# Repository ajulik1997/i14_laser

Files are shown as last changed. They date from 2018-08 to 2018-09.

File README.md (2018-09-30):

# I14 Remote Laser Controller

Software developed for the remote control and monitoring of a laser at the [Diamond Light Source I14 instrument](https://www.diamond.ac.uk/Instruments/Imaging-and-Microscopy/I14.html).

The following documentation is designed as a guide to simplify the processes of preparing the hardware and installing this software, as well as extending its functionality and applying it to other components or instruments.

## Table of Contents

- [Introduction](#introduction)
  - [Key Features](#key-features)
- [The Hardware](#the-hardware)
  - [Raspberry Pi](#raspberry-pi)
    - [Operating System](#operating-system)
    - [Drivers and Packages](#drivers-and-packages)
    - [Python](#python)
    - [Pin Assignment](#pin-assignment)
  - [Laser](#laser)
  - [Arduino](#arduino)
    - [Pin Assignment](#pin-assignment)
    - [LED Signalling](#led-signalling)
    - [Wiring Diagram](#wiring-diagram)
  - [Digital to Analog Converter](#digital-to-analog-converter)
    - [Safety](#safety)
    - [Laser modulation](#laser-modulation)
  - [Camera](#camera)
- [The Software](#the-software)
  - [Server](#server)
    - [Client](#client)
  - [Parser](#parser)
    - [Table of Recognised Commands](#table-of-recognized-commands)
  - [Error Handler](#error-handler)
    - [Table of Errors and Warnings](#table-of-errors-and-warnings)
  - [Laser Serial Communication Script](#laser-serial-communication-script)
  - [Arduino Controller Script (Python)](#arduino-controller-script-python)
    - [Arduino Controller Script (C for AVR)](#arduino-controller-script-c-for-avr)
- [Licensing](#licensing)
- [Author](#author)
- [Acknowledgements](#acknowledgements)

## Introduction

At the core of this "system" lies a [Raspberry Pi](https://www.raspberrypi.org/), used as a server running a python script which allows it to process text-based commands that it receives over network. A [Coherent Laser](https://www.coherent.com/) is connected to the Raspberry Pi via a USB-to-Serial interface, enabling the Pi to send commands to the laser and monitor its status. An [Arduino board](https://www.arduino.cc/) is also connected to the Raspberry Pi via a USB-to-Serial as well as a GPIO interface, and is mainly responsible for real-time generation of waveforms that are used to modulate the laser via a Digital-to-Analog converter (DAC). Additionally, a camera can also be connected to the Arduino, which can synchronise the camera's shutter with the modulation of the laser.

A diagram that illustrates this setup can be seen below. It was created using [draw.io](https://www.draw.io/), and the source can be downloaded [here](./resources/flowcharts/project_map.xml).

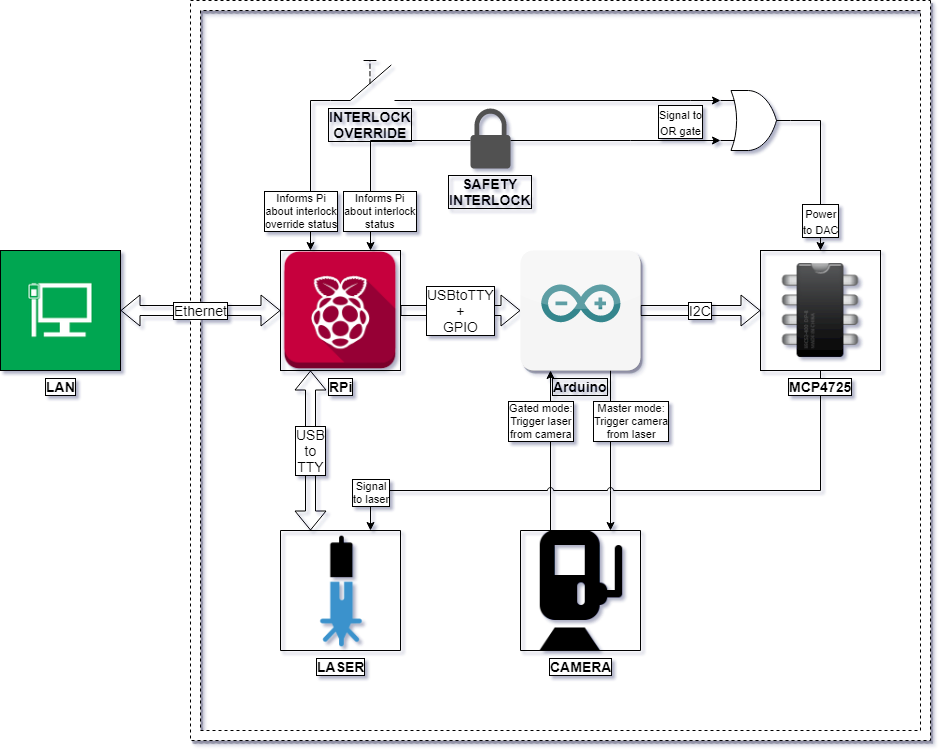
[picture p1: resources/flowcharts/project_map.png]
Project Map


### Key Features

The most noteworthy and desirable features of this project can be summarised as follows:

  - Remote control of laser over LAN
  - Remote monitoring of laser and safety interlock status over LAN
  - High-precision control of laser output intensity
  - Modulation of laser beam with pre-set waveforms of customisable period length and inter-cycle delay:
    - Sine wave, triangle wave, sawtooth wave: cycle period between 1 millisecond and 1 second
    - Square wave, pulse wave: cycle period between 1 millisecond and 1 hour
  - Synchronisation of laser with connected camera:
    - "gated mode": laser is turned on only when camera is exposing
    - "master mode": camera exposure triggered when laser intensity reaches a customisable threshold
  - Robust and extensible error handling
  - Modular, well-documented code for easy customisation

## The Hardware

The following section documents the steps required to correctly set up the hardware. It describes the setup of the operating system on the Raspberry Pi, as well as the required wiring between the Raspberry Pi, Arduino, DAC, laser and camera.

### Raspberry Pi

The Raspberry Pi used in this project is the [Raspberry Pi 3 B+](https://www.raspberrypi.org/products/raspberry-pi-3-model-b-plus/) (upgraded from the Raspberry Pi B Rev 2.0 on which development took place), chosen due to the following features:
  - 1.4GHz processor (upgraded from 700MHz)
  - 1GB SDRAM (upgraded from 512MB)
  - 40 GPIO pins (upgraded from 26)
  - Gigabit Ethernet
  - MicroSD port
  - PoE support

According to our specification, the Raspberry Pi needs to be set up so that it can do the following:
  - run a headless Linux OS
  - securely connect to a LAN
  - communicate with other devices on the LAN via SSH
  - communicate with laser via Serial-over-USB
  - communicate with Arduino via Serial-over-USB and GPIO
  - start Python server at boot and ensure it restarts on exit

#### Operating System

The operating system chosen for this project was [Raspbian Stretch Lite](https://www.raspberrypi.org/downloads/raspbian/), an OS based on Debian Stretch with no desktop interface, chosen for its minimal footprint and high compatibility with Raspberry Pi. The required image was downloaded from the [official mirror](https://downloads.raspberrypi.org/raspbian_lite_latest), and written to a 16GB microSD card according to the [installation instructions](https://www.raspberrypi.org/documentation/installation/installing-images/README.md).

As the Pi is being used a server, it needs to be set up to run headless. This process is described in detail [here](https://www.raspberrypi.org/documentation/configuration/wireless/headless.md), but the most important step (activating SSH), can be accomplished by mounting the boot partition of the SD card on any device and creating an empty file with the filename `ssh`. The contents of this file does not matter, as it will be deleted on boot, and SSH should be activated. Alternatively, it is possible to do the initial setup with an attached monitor and keyboard. Note that, on some networks, the MAC address of the Raspberry Pi will first need to be registered before any network communication can take place. In this scenario, using a monitor and keyboard initially is the easiest option.

Once it is possible to interface with the Raspberry Pi, either over SSH or physically, the Raspberry Pi configuration tool will need to be launched using:

```shell
sudo raspi-config
```

You will be presented with a terminal user interface (TUI) similar to the one below:

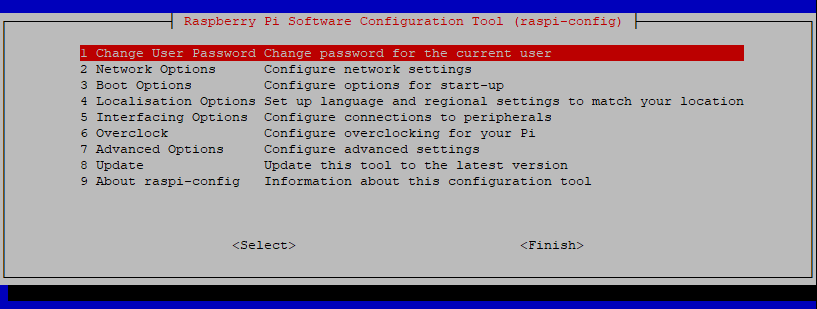
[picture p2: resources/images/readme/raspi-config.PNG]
raspi-config


The settings that will need be changed are:
  - **Change User Password**: change the user password so that it is not possible to start an SSH session with the Raspberry Pi using the default password
  - **Network Options**:
    - **Hostname**: change the name that the Raspberry Pi identifies itself as on the network (default is `raspberrypi`)
  - **Interfacing Options** (optional):
    - **Camera**: disable the CSI camera interface as we are not using it
    - **SSH**: enable the SSH interface if you have not done so already
    - **VNC**: disable the VNC as we are not running a desktop environment
    - **SPI**: disable the SPI interface and automatic loading of the SPI kernel module as we are not using it
    - **I2C**: disable the I2C interface and automatic loading of the I2C kernel module as we are not using it
    - **1-Wire** : disable the 1-Wire interface as we are not using it

If the device will only communicate over Ethernet, then we can disable WiFi and Bluetooth by adding the following lines to `/boot/config.txt`:

```shell
dtoverlay=pi3-disable-wifi
dtoverlay=pi3-disable-bt
```

Once Bluetooth has been disabled, `systemd` will encounter an error when loading the `hciuart` service. Although this error is harmless, in order to avoid the error message at boot, you can do:

```shell
sudo systemctl disable hciuart
```

Optionally, it is a good idea to disable all other services that we will not need. A full list of active `systemd` services is obtained by running `sudo systemctl list-unit-files | grep enabled`. Please inspect this list **carefully** before disabling all but the services you require. I have found that the following services are critical for normal operation of a minimal Raspberry Pi system:

- `autovt`: configures and manages virtual terminals
- `cron`: time-based job scheduler
- `dbus`: inter-process communication and message bus system
- `dhcpcd`: provides a DHCP service
- `fake-hwclock`: emulates a hardware clock on systems that don't have or support one
- `getty`: short for "get TTY", it manages physical or virtual terminals
- `networking`: manages all networking interfaces
- `rsyslog`: manages system logging
- `ssh`: SSH service
- `systemd`: system and service manager for Linux

To disable all enabled services except those listed above, execute:

```shell
sudo systemctl list-unit-files \
  | grep enabled \
  | cut -f 1 -d ' ' \
  | grep -v -E 'autovt|cron|dbus|dhcpcd|fake-hwclock|getty|networking|rsyslog|ssh|systemd' \
  | while read -r line; do sudo systemctl disable $line; done
```

To install an NTP client on the Raspberry Pi:

```shell
sudo apt-get update && sudo apt-get install ntp
```

If the Raspberry Pi is connected to a network without access to an NTP server, or you want to set the time before connecting to a network, you can do so with the following command:

```shell
sudo date -s "DD MMM YYYY HH:MM:SS"
```

##### Firewall setup

Firewall rules for the Raspberry Pi also need to be set up. Firstly, the default behaviour should be that the Pi will drop all incoming and forwarded packets, but allow all outgoing packets:

```shell
iptables -P INPUT DROP
iptables -P FORWARD DROP
iptables -P OUTPUT ACCEPT
```

Secondly, we should enable all communication on the `loopback` interface:

```shell
iptables -A INPUT -i lo -j ACCEPT
iptables -A OUTPUT -o lo -j ACCEPT
```

Additionally, we should allow all established sessions to communicate freely on the network:

```shell
iptables -A INPUT -m conntrack --ctstate ESTABLISHED,RELATED -j ACCEPT
```

Finally, we add exceptions to the default behaviour by allowing the following incoming packets:

```shell
iptables -A INPUT -p tcp --dport 22 -j ACCEPT       # SSH
iptables -A INPUT -p tcp --dport 14000 -j ACCEPT    # Python server
iptables -A INPUT -p udp --dport 123 -j ACCEPT      # NTP
iptables -A INPUT -p udp --dport 67:68 -j ACCEPT    # DHCP
```

##### Default user setup

It may be useful to also change the name and home directory of the default user from the default `pi`. To do this, first log in as the user `pi` and enable the `root` account by changing its password using `sudo passwd root` and entering a new password. Then, reboot the Raspberry Pi and log in as `root`, then execute:

```shell
usermod -l pi new_username
usermod -m -d pi new_username
```

Note that, these two commands cannot be carried out the same time according to the [documentation](https://linux.die.net/man/8/usermod), as changing the login name and the user's home directory have to be carried separately.

After that is done, reboot the system and log in to your new user account. From that account, you can again disable the `root` account by doing the following:

```shell
sudo su -c "usermod -L -e 1 root"
```

#### Drivers and Packages

This section highlights the packages and drivers that need to be installed or set up, either as dependencies by the server, or optional add-ons for easier development and set-up.

##### Flashing '.hex' files to Arduino

As of Arduino 1.6, it is possible to develop Arduino applications directly on the Raspberry Pi, although this is not recommended, as the newly released Arduino CLI has too many dependencies (up to 1GB, including a desktop environment, which is not necessary on a headless Raspberry Pi) for a system with limited storage and memory. Instead, it is recommended that all Arduino development is carried out elsewhere, and the compiled `.hex` can be sent to the Raspberry Pi via `scp`, then flashed onto the Arduino from the Raspberry Pi using `avrdude`.

`avrdude` is a software for programming Atmel AVR controllers, such as the ATmega328 that is at the core of the Arduino Duo. At the time of writing, `avrdude` was available for download using `apt-get`:

```shell
sudo apt-get install avrdude
```

Alternatively, you can download the latest source code from [here](http://download.savannah.gnu.org/releases/avrdude/), and compile from source.

Flashing a `.hex` file can then be accomplished by running the following command, explained below:

```shell
sudo avrdude -p atmega328p -P /dev/ttyACM0 -c arduino -U flash:w:arduino.hex:i
```

- `sudo` to give `avrdude` permission to access the USB device
- `-p atmega328p` to select the part number of the microcontroller (atmega328p for my Arduino Uno)
- `-P /dev/ttyACM0` to specify the communication port (change this if your Arduino is assigned a different port)
- `-c arduino` to specify the programmer type (`arduino` is the safest option, but a different setting may be needed depending on your chip)
- `-U flash:w:arduino.hex:i` is the command that does the actual programming
  - `flash` is the memory type we are flashing
  - `w` specifies write mode (which usually also carries out a verify pass after flashing)
  - `arduino.hex` is the filename of the `.hex` file we are flashing (change this to your filename)
  - `i` specifies that this file has the “Intel Hex” format

Many other options are also available, that may or not may be useful or necessary when doing your own development. A nice tutorial that highlights all the important options can be found [here](http://www.ladyada.net/learn/avr/avrdude.html).

##### Setting up USB laser as a Serial device

When the laser is first plugged in to the Arduino, it is not recognised as a device capable of serial input/output. Although the laser uses a standard FTDI chip, its VID/PID is not one recognised by Linux as a `ftdi_sio` device. Luckily, most modern Linux distributions (including Raspbian) have FTDI drivers built into their Kernel.

We start by creating a shell script `laserUSBtoSerial.sh` (alternatively, you can download it from [here](./laserUSBtoSerial.sh)):

```shell
#!/bin/bash
modprobe ftdi_sio
echo 0d4d 003d > /sys/bus/usb-serial/drivers/ftdi_sio/new_id
udevadm control --reload && udevadm trigger
```

`modprobe` adds an `ftdi_sio` module into the Linux kernel. Using `echo`, we then insert the Vendor ID (`0d4d` - registered by Coherent) and the Product ID (`003d` - specific to this laser model) into a file newly created by `modprobe`. This allows the kernel to associate a device that identifies itself using that VID/PID combination (our laser) with the relevant FTDI driver. Finally, for a change to be detected by the kernel, the USB device needs to unplugged (if it is plugged in), and re-plugged. If physical access to the device is not available as expected, `udevadm` is used to reload the udev rules and trigger a USB plug-in event.

This script needs to be executed with superuser privileges after every reboot:

```shell
sudo su -c "./laserUSBtoSerial.sh"
```

In order to avoid having to manually run the script, it is recommended to install it a `systemd` service that will run this script once at boot.

We will create a `.service` file in the path `/lib/systemd/system/` called `laserUSBtoSerial.service` as follows (or download it from [here](./laserUSBtoSerial.service)):

```shell
[Unit]
Description=Enable Coherent Laser USB-to-Serial

[Service]
Type=forking
ExecStart=/home/pi/laserUSBtoSerial.sh

[Install]
WantedBy=multi-user.target
```

For the sake of brevity, the options specified in this `systemd.service` file will not be explained here. Instead, a page that gives in-depth explanations and usage examples of all the available options can be viewed [here](https://www.freedesktop.org/software/systemd/man/systemd.service.html).

Once the file is created, its permission will need to be changed to allow execution:

```shell
sudo chmod 744 laserUSBtoSerial.sh
```

Finally, the `.service` will need to be enabled:

```shell
sudo systemctl enable laserUSBtoSerial.service
```

At this point, the service should be set up to execute our script at boot. To test whether the service is configured properly, you can execute `sudo systemctl start laserUSBtoSerial` , or simply reboot the device. Then, check the status of the service using `sudo systemctl status laserUSBtoSerial` (the presence of any errors will be highlighted in red, and point to an incorrect setup of the service).

#### Python

The server for the Raspberry Pi was written in `Python3` and tested on `3.5.3`, which was the version that came preinstalled with operating system. The list of non-trivial libraries that the server and parser depend on are:

- `RPi.GPIO`: for control of GPIO pins
- `serial`: for serial communication with connected devices
- `socket`: needed for accessing the BSD socket interface
- `threading`: needed for a threaded server

Out of these, `RPi.GPIO` and `serial` are not included in Python's Standard Library (`RPi.GPIO`, however, comes preinstalled for `Python2` with Raspberry Pi). These libraries will need to be installed manually:

```shell
sudo apt-get install python3-rpi.gpio
sudo apt-get install python3-serial
```

#### Pin Assignment

The pinout of the Raspberry Pi can be seen in the image below (obtained from [pinout.xyz](https://pinout.xyz/resources/raspberry-pi-pinout.png)):

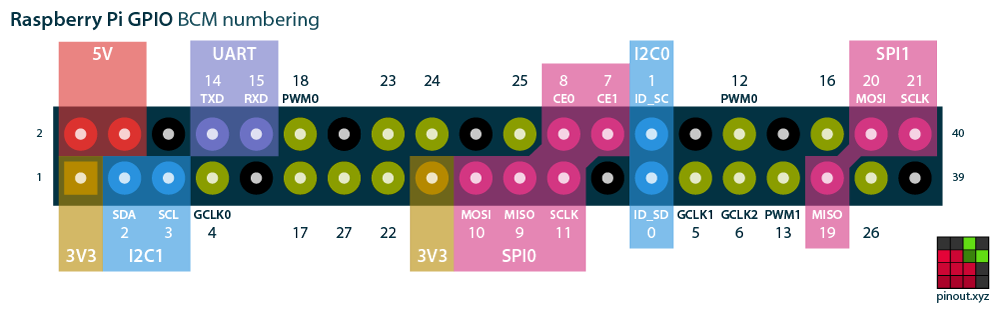
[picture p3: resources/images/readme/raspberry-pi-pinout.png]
Raspberry Pi Pinout


A large number of the GPIO pins available to us are, or can be, used for other purposes, such as I2C, SPI, and UART. The pins assigned in this project have been carefully selected to not overlap with any of these interfaces, not because they are being used in this project, but because in the scenario where their use becomes useful, the pins will not need to be moved and the code will not need to be edited. The following table describes the pin assignment used for the Raspberry Pi.

| GPIO (BCM) Pin Number | Physical Pin Number |         Assignment        | Input / Output |                                                             Description                                                             |
|:---------------------:|:-------------------:|:-------------------------:|:--------------:|:-----------------------------------------------------------------------------------------------------------------------------------:|
|           0           |          27         |         UNASSIGNED        |                |                                                     Used by Raspberry Pi for I2C                                                    |
|           1           |          28         |         UNASSIGNED        |                |                                                     Used by Raspberry Pi for I2C                                                    |
|           2           |          3          |         UNASSIGNED        |                |                                                     Used by Raspberry Pi for I2C                                                    |
|           3           |          5          |         UNASSIGNED        |                |                                                     Used by Raspberry Pi for I2C                                                    |
|           4           |          7          |         UNASSIGNED        |                |         Used by Raspberry Pi for GPCLK, allows the Pi to be set up to output a fixed frequency without any software control         |
|           5           |          29         |         UNASSIGNED        |                |         Used by Raspberry Pi for GPCLK, allows the Pi to be set up to output a fixed frequency without any software control         |
|           6           |          31         |         UNASSIGNED        |                |         Used by Raspberry Pi for GPCLK, allows the Pi to be set up to output a fixed frequency without any software control         |
|           7           |          26         |         UNASSIGNED        |                |                                                   Used by the Raspberry Pi for SPI                                                  |
|           8           |          24         |         UNASSIGNED        |                |                                                   Used by the Raspberry Pi for SPI                                                  |
|           9           |          21         |         UNASSIGNED        |                |                                                   Used by the Raspberry Pi for SPI                                                  |
|           10          |          19         |         UNASSIGNED        |                |                                                   Used by the Raspberry Pi for SPI                                                  |
|           11          |          23         |         UNASSIGNED        |                |                                                   Used by the Raspberry Pi for SPI                                                  |
|           12          |          32         |         UNASSIGNED        |                |                                              Used by the Raspberry Pi for Hardware PWM                                              |
|           13          |          3          |         UNASSIGNED        |                |                                              Used by the Raspberry Pi for Hardware PWM                                              |
|           14          |          8          |         UNASSIGNED        |                |                                                  Used by the Raspberry Pi for UART                                                  |
|           15          |          10         |         UNASSIGNED        |                |                                                  Used by the Raspberry Pi for UART                                                  |
|           16          |          36         |  SAFETY INTERLOCK STATUS  |     OUTPUT     |     A combination of 2 of the Operation Mode Selector pins will signal the Arduino to switch to the corresponding operation mode    |
|           17          |          11         |  MODULATION MODE SELECTOR |     OUTPUT     | A combination of 3 Modulation Mode Selector pins will signal the Arduino to output one of the corresponding preprogrammed waveforms |
|           18          |          12         |         UNASSIGNED        |                |                                                  Used by the Raspberry Pi for UART                                                  |
|           19          |          35         |         UNASSIGNED        |                |                                                   Used by the Raspberry Pi for SPI                                                  |
|           20          |          38         |         UNASSIGNED        |                |                                                   Used by the Raspberry Pi for SPI                                                  |
|           21          |          40         |         UNASSIGNED        |                |                                                   Used by the Raspberry Pi for SPI                                                  |
|           22          |          15         |  MODULATION MODE SELECTOR |     OUTPUT     | A combination of 3 Modulation Mode Selector pins will signal the Arduino to output one of the corresponding preprogrammed waveforms |
|           23          |          16         |  OPERATION MODE SELECTOR  |      INPUT     |                                             Monitors the status of the safety interlock                                             |
|           24          |          18         |  OPERATION MODE SELECTOR  |      INPUT     |                                         Monitors the status of the safety interlock override                                        |
|           25          |          22         |       ARDUINO RESET       |     OUTPUT     |                           Turning on this pin will reset the Arduino and bring back to a known safe state                           |
|           26          |          37         | INTERLOCK OVERRIDE STATUS |     OUTPUT     |     A combination of 2 of the Operation Mode Selector pins will signal the Arduino to switch to the corresponding operation mode    |
|           27          |          13         |  MODULATION MODE SELECTOR |     OUTPUT     | A combination of 3 Modulation Mode Selector pins will signal the Arduino to output one of the corresponding preprogrammed waveforms |

### Laser

The laser used in this project is the [Coherent BioRay](https://www.coherent.com/lasers/laser/stingray-and-bioray-lasers) laser, controlled by a corresponding Coherent BioRay Controller unit, as specified in the [documentation](https://edge.coherent.com/assets/pdf/Coherent-BioRay-Operator-s-Manual.pdf).

The back panel of the controller unit has the following connectors (alternatively, see Figure 4-2. in the documentation):

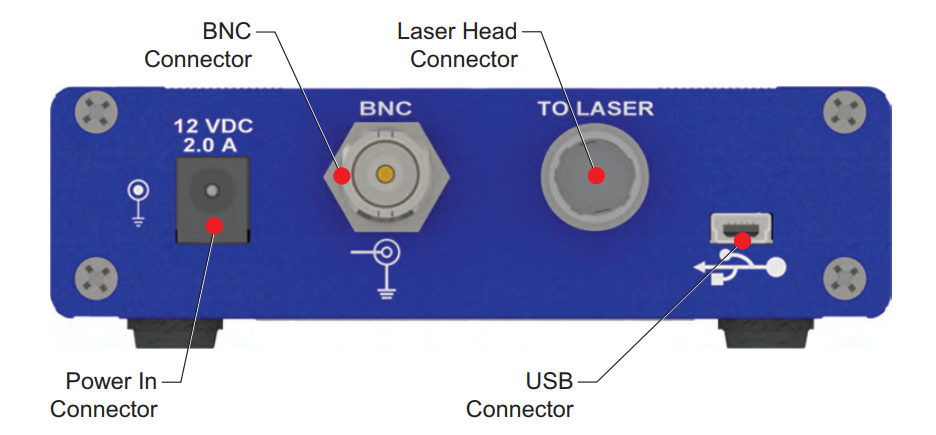
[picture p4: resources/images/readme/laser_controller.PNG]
Laser Controller


The controller unit receives power via the *Power In Connector*, and in turns supplies power to the laser via the *Laser Head Connector* into which the laser itself is connected. The *BNC connector* allows signals and waveforms to be sent to the laser controller, which will modulate the laser according to the following diagram (alternatively, Figure 2-1 in the documentation):

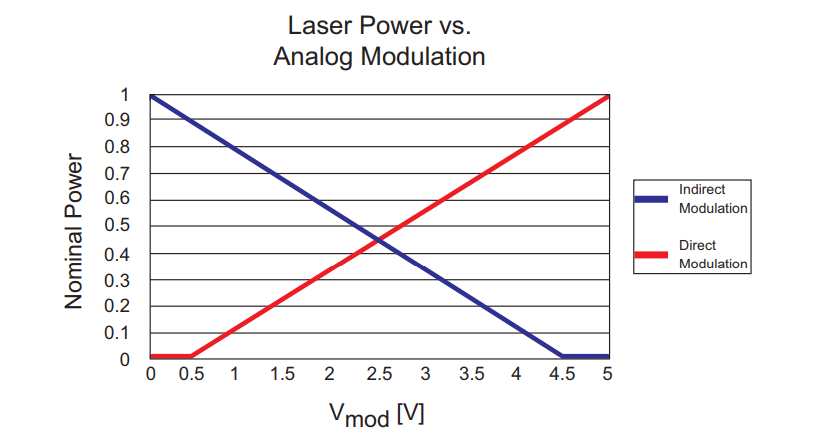
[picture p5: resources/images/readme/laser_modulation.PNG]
Laser Modulation Curve


The *Mini USB B* connector allows commands to be sent to the laser via RS-232 over USB. The laser supports many different commands for changing the settings or getting the status of the laser (full list can be seen as Table 5-1. in the documentation), most of which will not be used in this project. The Raspberry Pi communicates directly with the laser by sending and receiving serial data via a USB A to Mini USB B cable connected to the controller.

### Arduino

The Arduino used in this project is the [Arduino Uno](https://store.arduino.cc/arduino-uno-rev3), used as a smart modulation controller for the laser described above. This specific Arduino was chosen due to its small size as well as the following features:

- 5V operating voltage (same as the Raspberry Pi)
- 14 digital I/O pins (6 are hardware PWM output pins)
- 6 analog input pins
- 32KB of Flash Memory
- 2KB of SRAM
- 16MHz clock speed

According to our specification, the Arduino will need to be setup up to be able to do the following:

- receive Serial messages from the Raspberry Pi
- read GPIO pins to determine the modulation mode and operation mode
- send I2C data to a connected DAC
- generate waveforms of different shape, amplitude and frequency
  - allow all waveforms to trigger camera at a user-defined threshold
  - allow some waveforms to be triggered by a camera
- signal status using LED and piezo buzzer
- detect (hardware and software) the breaking of the safety interlock
- visually and audibly warn when overriding the safety interlock

#### Pin Assignment

This section will describe what every pin on the Arduino will be set up to do, as well as how the Arduino will be wired with other components. A very nice diagram of the full Arduino pinout can be seen on [circuito.io](https://www.circuito.io/blog/arduino-uno-pinout/), from which I have taken snippets and included below.

The Arduino has 14 digital IO pins, marked as 0 to 13 in purple on the diagram below:

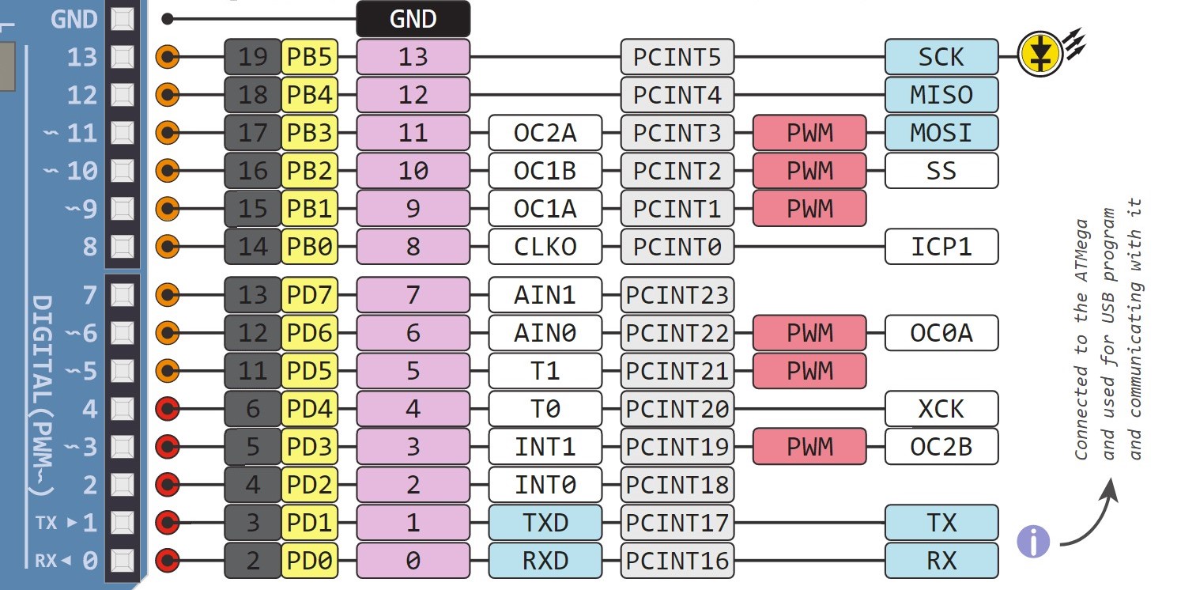
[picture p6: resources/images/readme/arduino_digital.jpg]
Arduino Digital IO Pins


The assignment of these digital pins is summarised as follows:

| Pin Number |        Assignment       | Input/Output/PWM |                              Description                              |
|:----------:|:------------------------:|:----------------:|:---------------------------------------------------------------------:|
|      0     |        UNASSIGNED        |                  |              Used by the Arduino for serial communication             |
|      1     |        UNASSIGNED        |                  |              Used by the Arduino for serial communication             |
|      2     |       LASER TRIGGER      |       INPUT      |     Enables connected camera to trigger laser pulses when exposing    |
|      3     |      CAMERA TRIGGER      |      OUTPUT      | Enables laser to synchronise camera shutter with a generated waveform |
|      4     | MODULATION MODE SELECTOR |       INPUT      |          Activates one of the preprogramed modulation modes          |
|      5     |         POWER LED        |        PWM       |                 Controls intensity of green power LED                 |
|      6     |          BUZZER          |        PWM       |                        Controls tone of buzzer                        |
|      7     | MODULATION MODE SELECTOR |       INPUT      |          Activates one of the preprogramed modulation modes          |
|      8     | MODULATION MODE SELECTOR |       INPUT      |          Activates one of the preprogramed modulation modes          |
|      9     |         [R]GB LED        |        PWM       |              Controls intensity of red colour in RGB LED              |
|     10     |         RG[B] LED        |        PWM       |              Controls intensity of blue colour in RGB LED             |
|     11     |         R[G]B LED        |        PWM       |             Controls intensity of green colour in RGB LED             |
|     12     |        UNASSIGNED        |                  |                                 Unused                                |
|     13     |        UNASSIGNED        |                  |                          Used by built-in LED                         |

The Arduino also has 6 analog input pins, marked as A0 to A5 in green on the diagram below:

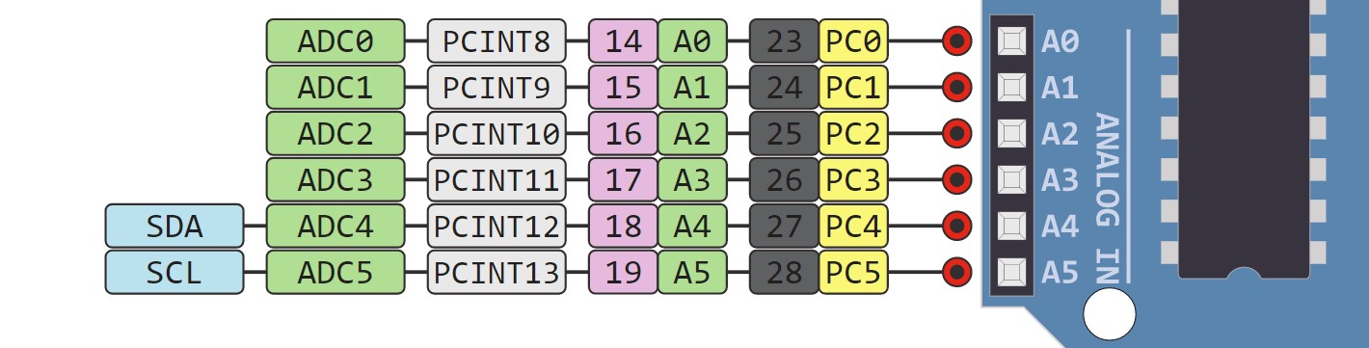
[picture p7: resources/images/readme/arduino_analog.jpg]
Arduino Analog Input Pins


The assignment of the analog pins is summarised by the following table:

| Pin Number |       Assignment       |                      Description                     |
|:----------:|:-----------------------:|:----------------------------------------------------:|
|     A0     | OPERATION MODE SELECTOR |   Activates one of the preprogramed operation modes  |
|     A1     | OPERATION MODE SELECTOR |   Activates one of the preprogramed operation modes  |
|     A2     |    INTERLOCK MONITOR    |      Monitors the status of the safety interlock     |
|     A3     |     OVERRIDE MONITOR    | Monitors the status of the safety interlock override |
|     A4     |        UNASSIGNED       |         Used by Arduino for I2C communication        |
|     A5     |        UNASSIGNED       |         Used by Arduino for I2C communication        |

It is important to note that:
- For any digital pin, the Arduino defines voltages below 0.8V as LOW and voltages above 2V as HIGH. If any digital input pin has a voltage between 0.8V and 2V, its state is "undefined". That is why it is important to use **pull-down resistors** (or pull-up resistors, but none have been used in this project), to make sure the pin is pulled down below 0.8V when no voltage is applied, so the pin can be read as LOW. The pull-down resistors used in the project are all 2.2 kohm.
- The recommended maximum current that a single pin can take/provide is 20mA.
- The absolute maximum current that all pins can take/provide together is 200mA.

##### Resetting Arduino

It will sometimes be necessary to bring the Arduino back to a "known safe state", for example after a power loss of the Raspberry Pi, the internal variables of the server will need to be reinitialised and match those on the Arduino. We do this by connecting the "RESET" pin on the Arduino (see image below) to an NPN Transistor (for example, [this one](https://www.sparkfun.com/datasheets/Components/BC546.pdf)). The *collector* of the transistor would connect to the RESET pin, while the *emitter* would be connected to ground. The *base* of the transistor will be set up to connect to a pin on the Raspberry Pi, which can then trigger the reset of the Arduino.

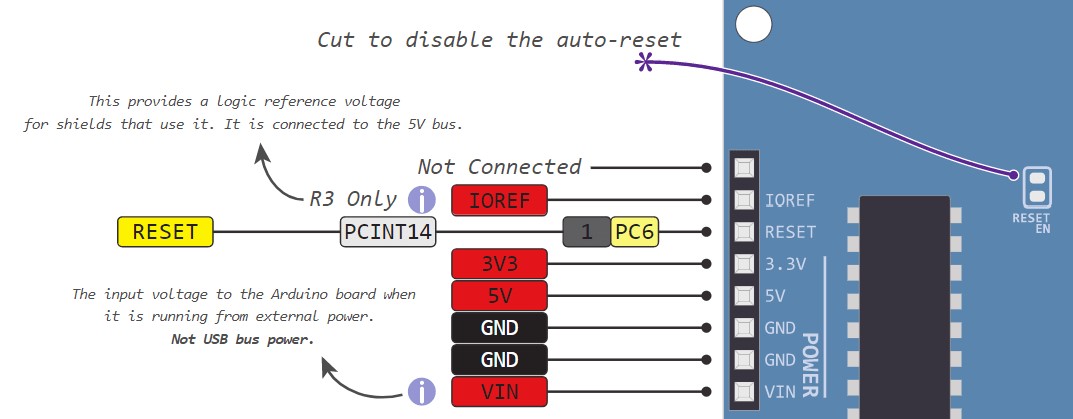
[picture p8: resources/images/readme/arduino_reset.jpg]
Arduino Reset Pin


It is important to note that, when the transistor is *saturated* (see [here](https://learn.sparkfun.com/tutorials/transistors/operation-modes)), it is essentially acting like a short-circuit and therefore damaging the transistor as well as the GPIO pin on the Raspberry Pi. Therefore, an appropriate resistor needs to be wired between the transistor *base* and the GPIO pin (I have used the same resistor as those used for pull-down).

#### LED Signalling

A green "power" LED as well as an RGB "status" LED is used to signal different events or states that the Arduino is in. The list of all possible colour combinations, as well as their meaning, can be seen in this table:

|           Status           | Power LED (green) |   Status LED (RGB)   |                         Description                          |
| :------------------------: | :---------------: | :------------------: | :----------------------------------------------------------: |
|         Power off          |        Off        |         Off          |   The device is not receiving power or is being programmed   |
|          Booting           |       Green       |      RGB cycle       |           The device is in the process of booting            |
|           Ready            |       Green       |         Off          |   The device is ready and waiting to receive instructions    |
|      Lasing (normal)       |       Green       |  Blue (continuous)   | The device is device is modulating the laser with a non-zero amplitude continuous wave, sine wave, triangle wave or sawtooth wave |
|      Lasing (pulsed)       |       Green       |  Blue (intermittent)  | The device is modulating the laser with a square wave or a pulse train, where the RGB LED will be illuminated synchronously with the laser |
|        Calibrating         |       Green       | Magenta (continuous) | The device is undergoing a calibration pass after it has received new wave parameters. |
|       Receiving data       |       Green       |  Green (continuous)  | The device is receiving or parsing data received from an attached serial device |
|   Safety Interlock Open    |       Green       |   Red (continuous)    | The device detected that the safety interlock is open and is not being manually overridden, therefore laser modulation has been temporarily disabled. |
| Safety Interlock Overridden |       Green       | Orange (intermittent) | The device detected that the safety interlock is open but it is being manually override. Laser modulation is enabled but an audible warning will sound (if enabled) synchronously with the orange warning light. |

#### Wiring Diagram

This section describes the required wiring between all the components and the Arduino, using photographs of the setup accompanied by a schematic diagram. The wiring of the entire system, including the DAC, safety gate, interlock and switch terminals, remote reset transistor, indicator LEDs, warning piezo buzzer, and camera communication connections, can be seen in the image below, followed by a full schematic.

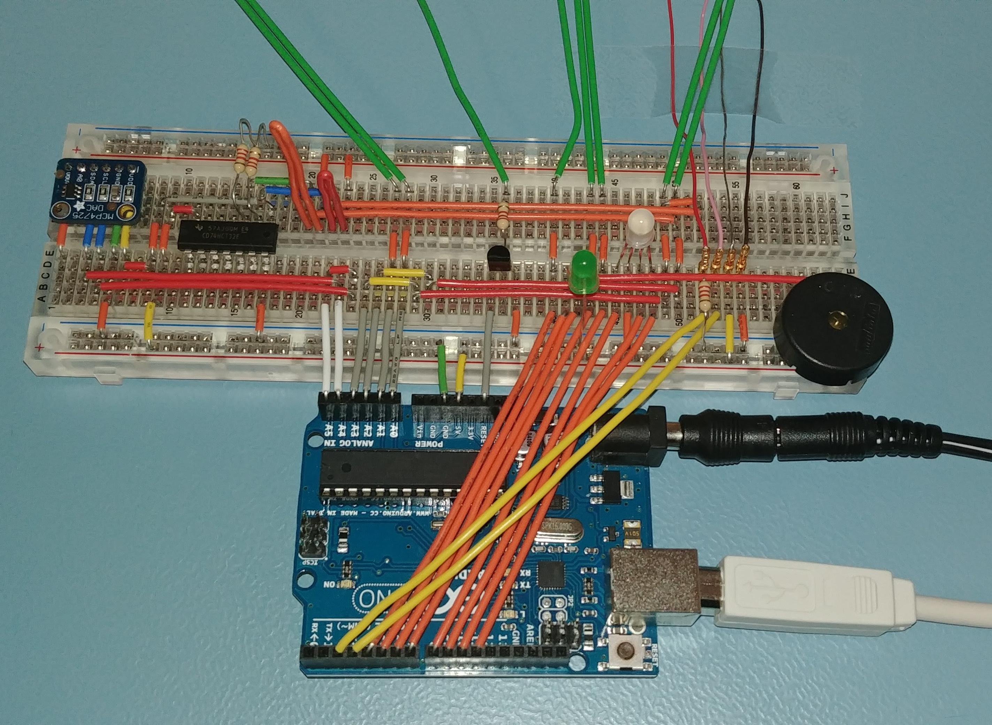
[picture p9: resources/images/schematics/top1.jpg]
Full_Schematic_Image


The schematic below was created using [Fritzing](www.fritzing.org). The Fritzing source file is also available [here](resources/schematics/full_schematic.fzz). Anyone wishing to clean up this wiring and transfer it to a PCB should find the Fritzing schematic very useful.

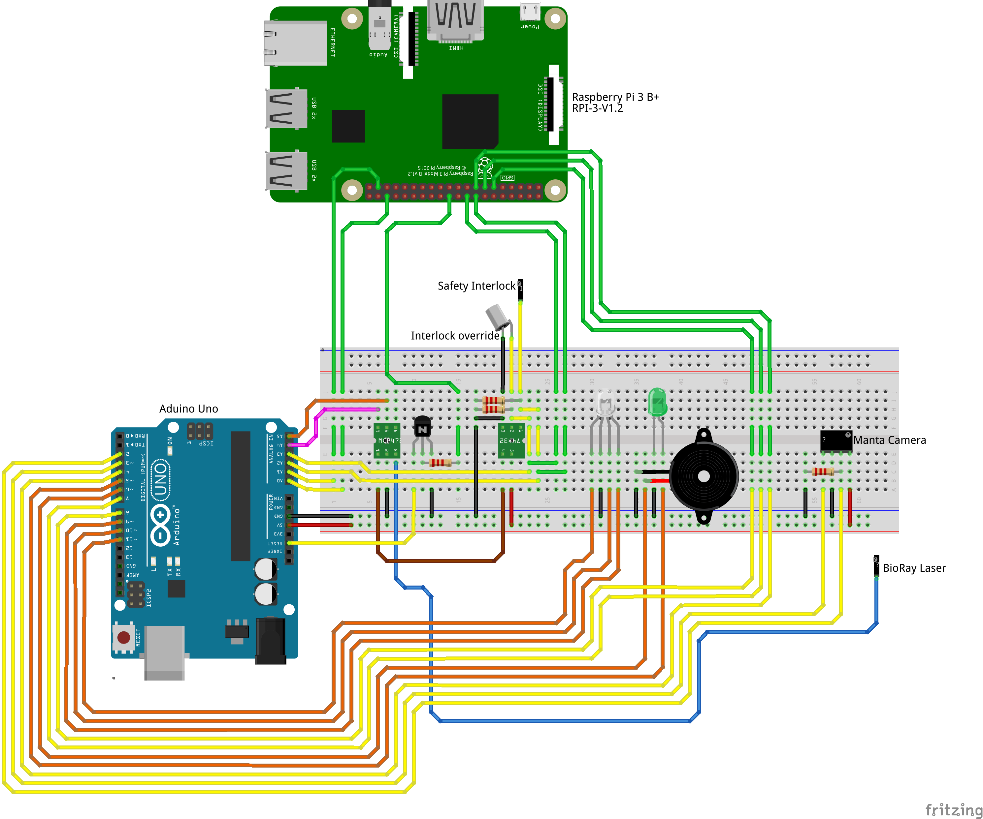
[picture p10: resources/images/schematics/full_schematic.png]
Full_Schematic


Although care has taken to reserve different jumper colours for each "type" of connection, due to lack of sizes, some colours had to be reused. The general rule is that **long green** jumpers correspond to connections with Raspberry Pi GPIO pins, while **long orange** jumpers connect breadboard components to the Arduino, and the **long yellow** jumpers connect the Arduino to the camera. Additionally, **mid-sized grey and white** jumpers are connections between the Arduino's "analog out" pins and the breadboard. It should be noted that small jumpers with same colours have also been used for inter-breadboard connections. A more consistent colouring scheme has been used in the Fritzing schematic:

| Colour |        Meaning       |
|:------:|:--------------------:|
|  Black |        Ground        |
|   Red  |       5V Power       |
|  Brown |  0-5V Variable Power |
|  Green |      3.3V Signal     |
| Yellow |       5V Signal      |
| Orange |     5V PWM Signal    |
|  Pink  |      I2C Signal      |
|  Blue  | 0-5V Signal to Laser |

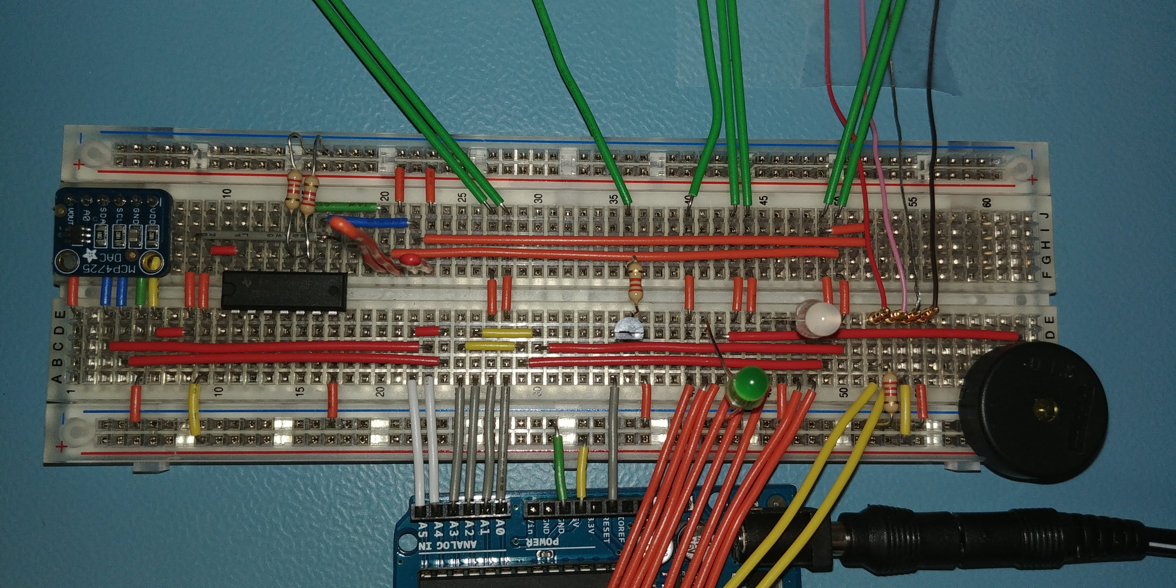
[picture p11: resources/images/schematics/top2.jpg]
Top2_Schematic_Image


We will begin by looking at the main breadboard. Starting from the left of the top half, the first component (rows 1-6) is the DAC, followed by an OR gate (rows 10-17), the safety interlock override switch terminals (rows 20-21) and the safety interlock monitor terminals (rows 22-23). The bottom half contains the Arduino remote reset transistor (rows 30-32), a green power LED, a status RGB LED (rows 45-48), followed by the camera communication connections (rows 52-55), and finally the warning piezo buzzer.

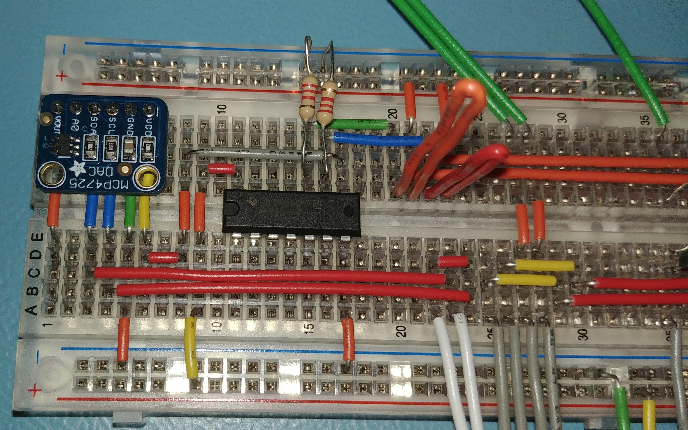
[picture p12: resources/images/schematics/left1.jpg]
Left1_Schematic_Image


This close-up highlights the connections between the DAC and the safety gate. The `VOUT` pin is connected to the laser via a BNC cable, and provides it a modulation signal. The `SDA` and `SCL` pins connect to Arduino's analog pins (blue-red-yellow), and allow for I2C communication with the DAC. `GND` is connected to the ground, while `VDD` is connected to the output pin of the OR gate (yellow-red-orange-grey). The OR gate is connected to 5V and ground, and takes two input. Input `A` is signal from the safety interlock override switch, and input `B` is the signal from the safety interlock. Both signals are pulled down to ground with an appropriate resistor.

It should be noted that some of the connections below are schematically correct but do not match the actual wiring, mainly due to inconsistencies between pinouts of different components.

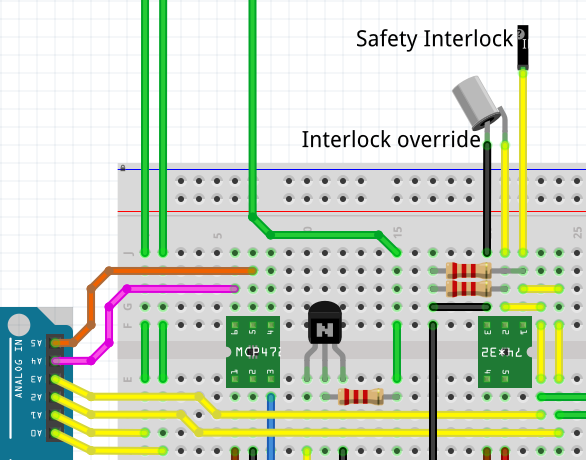
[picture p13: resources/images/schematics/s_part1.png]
Part1_Schematic


The image below is a close-up of the safety interlock (red curl) and override (yellow curl) terminals. They are connected to the OR gate via a short blue and green jumper, respectively

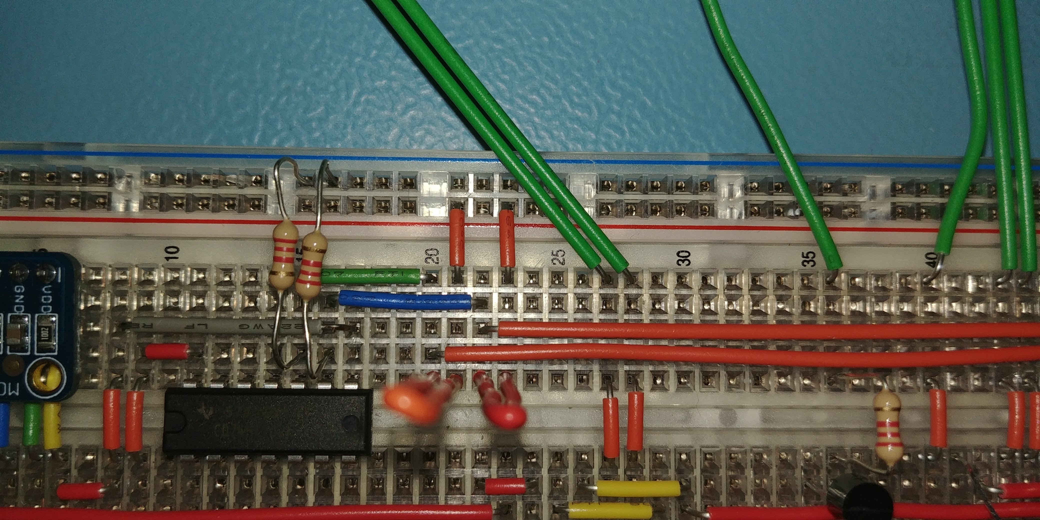
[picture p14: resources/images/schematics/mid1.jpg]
Mid1_Schematic_Image


The interlock and override terminals are also connected to RPi GPIO pins (via orange-green), as well as Arduino's analog-out pins (via orange-orange-(orange)-red-yellow-grey).

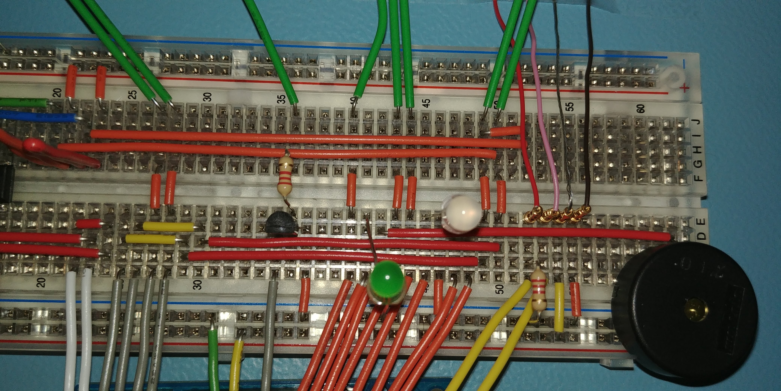
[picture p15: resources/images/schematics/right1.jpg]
Right1_Schematic_Image


The next view highlights the Arduino remote reset transistor, as well as the two signal LEDs. The emitter of the transistor is connected to the ground, while base is connected to one RPi GPIO trough a current-limiting resistor. The collector connected to the `RESET` pin on the Arduino. The green power LED is connected to one of Arduino's PWM pins and directly to ground, and will remain on while the Arduino is on. The RBG LED is connected in a similar fashion, but uses three PWM pins for the red, green and blue pins.

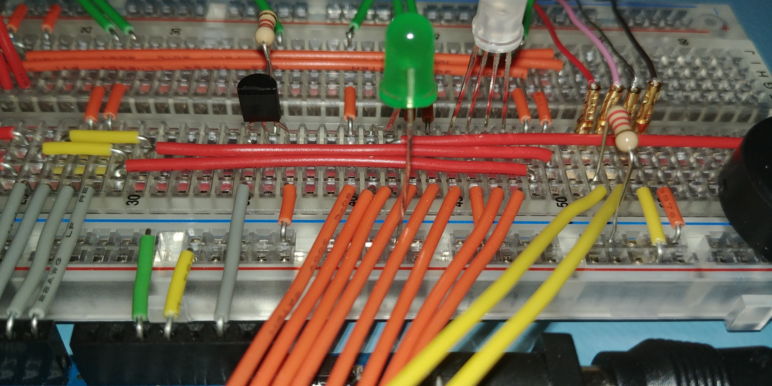
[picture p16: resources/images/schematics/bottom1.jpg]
Bottom1_Schematic_Image


The image below shows the final close up, this time of the camera communication connections and the piezo buzzer. The buzzer is connected in the same fashion as the LEDs: one pin to Arduino's PWM and the other to ground (in no particular orientation). The camera communication wires are highlighted red, pink, metallic, and brown. The red and pink wires corresponds to camera synchronisation pins, allowing the camera shutter to synchronise with the modulation waveform of the laser. They are connected to Arduino's GPIO pins, and the input pin is also pulled down to ground with an appropriate resistor. The metallic and brown pins provide isolated power and ground to the camera, for synchronisation purposes. These are connected to 5V and ground, respectively.

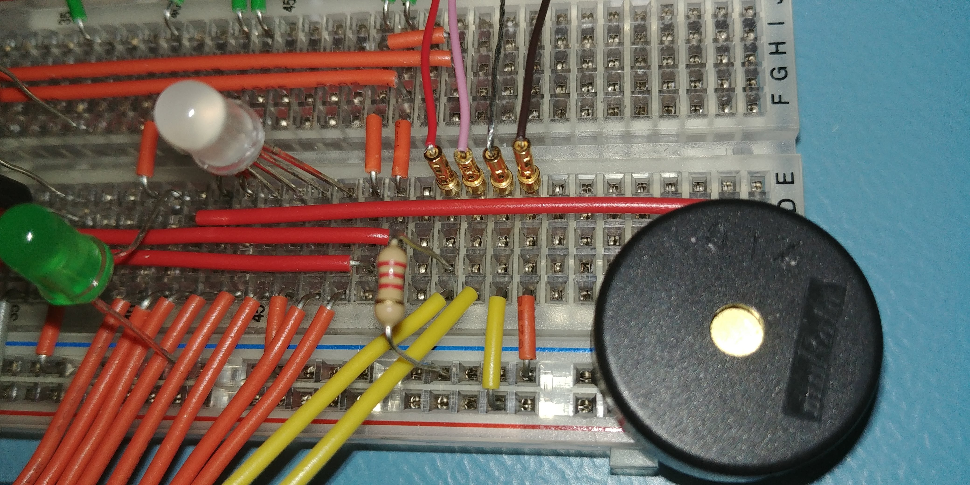
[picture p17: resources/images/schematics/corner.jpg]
Corner_Schematic_Image


Here is an alternate view showing all the signalling components as well as the camera communication connections.

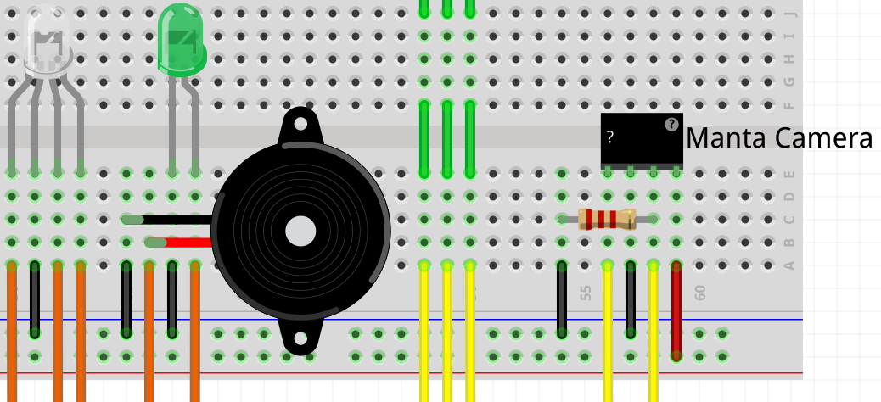
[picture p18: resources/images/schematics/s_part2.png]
Part2_Schematic


This final image shows all the connections leaving the Arduino. The two long yellow wires leaving the top of the Arduino (bottom of the image) connect to the camera. The orange wires on the same side lead to other components. These can be seen in more detail in the schematic, as well as in the table included in the sections above. The bottom of the Arduino has the "analog in" and "power" headers. The two white jumpers are used for I2C communication with the DAC, while the grey jumpers are used for other digital-through-analog connections. The green wire from the power header provides ground for the breadboard (-) rail, while the yellow provides 5V for the (+) rail. Finally, the grey jumper from the power rail connects the `RESET` pin to a transistor.

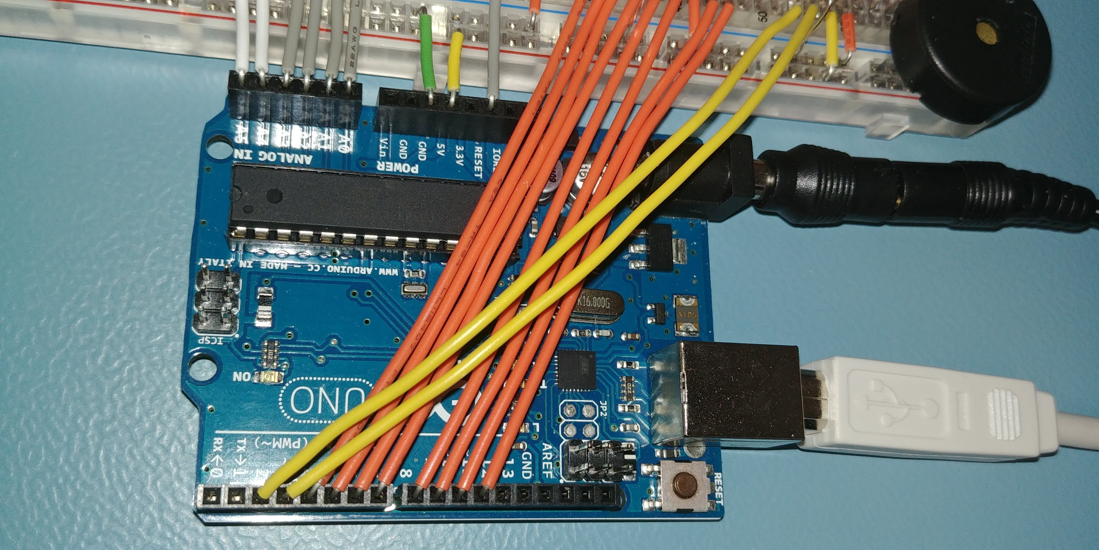
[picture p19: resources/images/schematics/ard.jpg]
Ard_Schematic_Image


This is the schematic view of the image above. The colours are consistent with the system described above. Note that this is a rotated view of a part of the schematic.

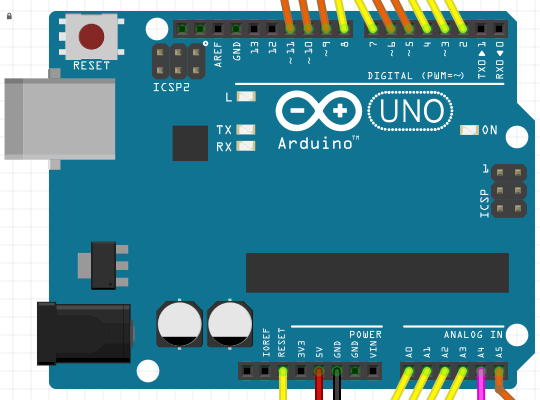
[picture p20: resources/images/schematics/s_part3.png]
Part3_Schematic


### Digital to Analog Converter

The digital-to-analog converter (DAC) used in the project is the 12-bit [MCP4725](https://cdn-shop.adafruit.com/datasheets/mcp4725.pdf) on an [Adafruit breakout board](https://www.adafruit.com/product/935). A useful tutorial by Adafruit on how to use the DAC with both Arduino and Raspberry Pi can be found [here](https://learn.adafruit.com/mcp4725-12-bit-dac-tutorial).

The DAC receives data from the Arduino using the I2C interface, where the DAC is the slave device and Arduino is the master. The DAC's `SCL` and `SDA` pins connect directly to Arduino's `SCL [A5]` and `SDA [A4]` pins. The DAC receives 5V through its `VDD` pin, and can output any voltage between 0V and 5V with a 12-bit accuracy through its `VOUT` pin.

#### Safety

Instead of the DAC being connected directly to Arduino's 5V output, it is powered through a logical OR gate (see [datasheet](http://www.ti.com/lit/ds/symlink/cd54hc32.pdf)) which takes two inputs: safety interlock, and interlock override. If the safety interlock is open (safety interlock line goes LOW), and the interlock override is not switched on (override line is also LOW), the gate will switch off the 5V output. As the DAC loses power, it can no longer output any signal, thereby modulating the laser beam to zero.

Additionally, once the DAC's power returns (either the interlock is closed or the override is turned on), the DAC's EEPROM has been set up so that it resumes to a safe state (output of 0V). The DAC will therefore have to be explicitly told to restart modulating the laser.

#### Laser Modulation

The Arduino has been programmed with 6 different modulation modes. If modulation is set to `none`, a waveform will not be generated, but a continuous wave of adjustable amplitude will be outputted. At an amplitude of 100%, the laser output looks like the image below, and looks analogous to how it operated before this project.

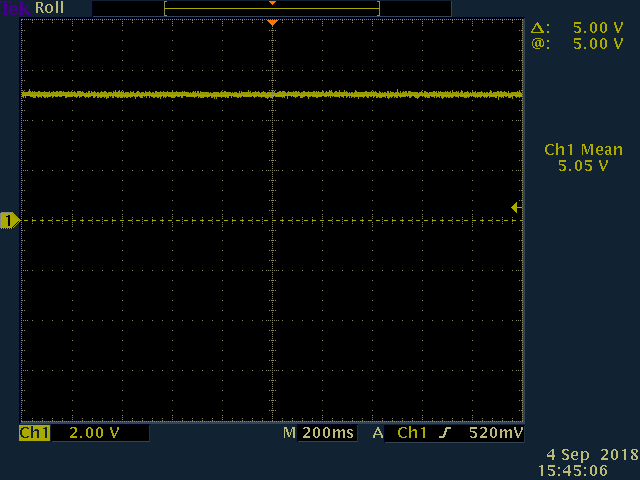
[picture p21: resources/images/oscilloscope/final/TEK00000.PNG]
Oscilloscope_none_100


The amplitude of the continuous wave can be set to any value between 0% and 100%. Here is the oscilloscope output for a continuous wave, this time at 42% amplitude.

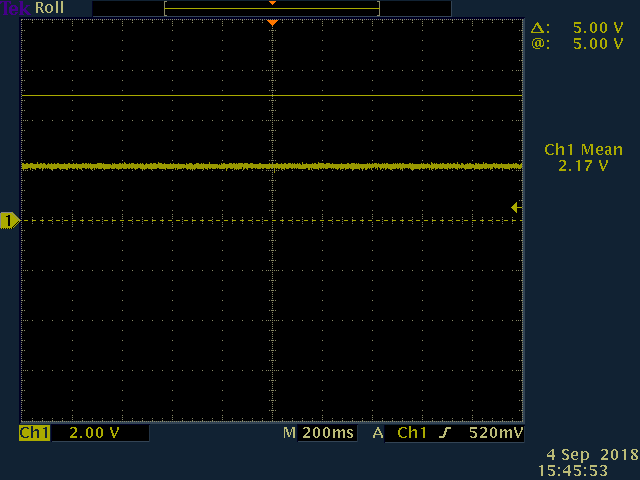
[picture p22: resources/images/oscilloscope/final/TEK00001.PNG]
Oscilloscope_none_42


The second modulation mode is `sine`. This mode generates a sine wave with a custom amplitude and period. The image below shows a sine wave at 100% amplitude with a period of exactly 100 milliseconds.

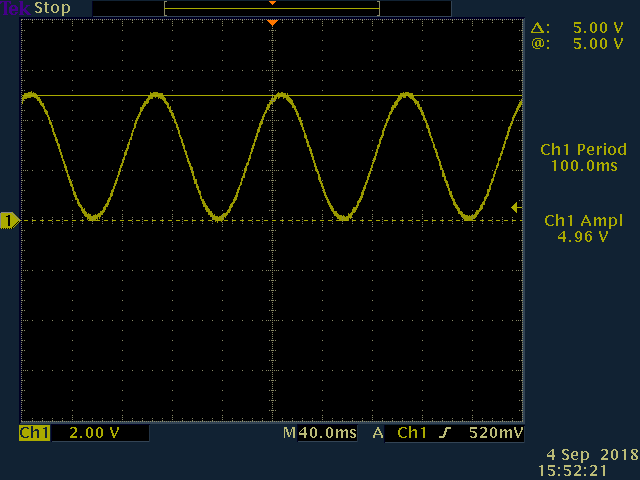
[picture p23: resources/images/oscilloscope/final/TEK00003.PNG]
Oscilloscope_sine_100


The amplitude of any wave can be changed. For the sake of brevity, not every waveform will be included with a range of amplitudes in this documentation. The following image is also a 100 millisecond sine wave, but this time with an amplitude of about 42%

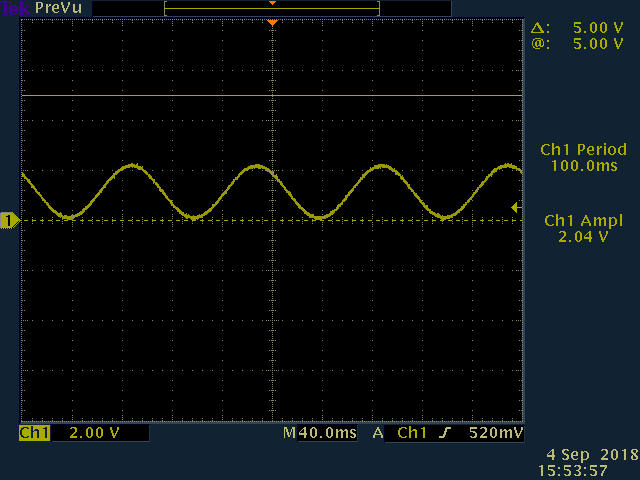
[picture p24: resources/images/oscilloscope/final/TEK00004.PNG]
Oscilloscope_sine_42


An additional parameter can be specified for any wave: the delay between every successive cycle. The wave below is a 100ms period wave with a delay of 200ms between waves, creating a total period of exactly 300ms.

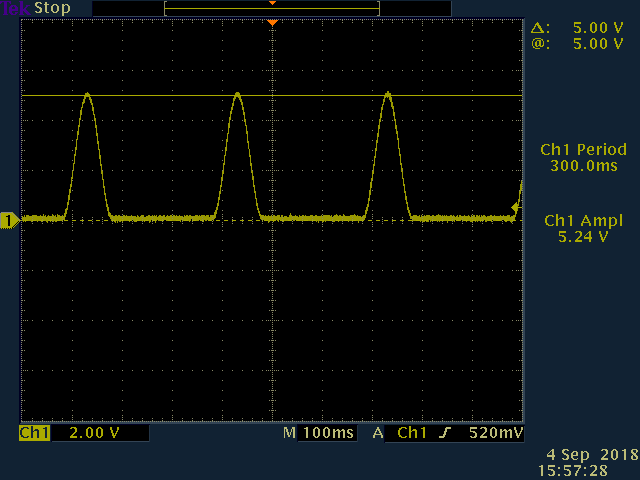
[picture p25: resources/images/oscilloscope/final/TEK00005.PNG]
Oscilloscope_sine_100_wait


If the operation mode of the Arduino is set to `master`, then the Arduino will output a HIGH when the amplitude of a wave reaches a user-defined threshold. This output, shown in blue, can be used to synchronise the laser modulation with the shutter of a camera (for example, only exposing when the laser is illuminating the sample adequately).

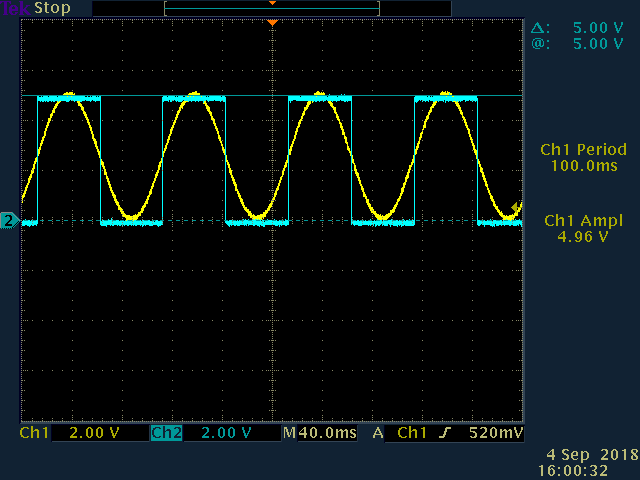
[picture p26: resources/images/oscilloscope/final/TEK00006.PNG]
Oscilloscope_sine_100_threshold_50


The previous image showed the trigger threshold at 50%. The following image shows the behaviour when the threshold is raised to 80%

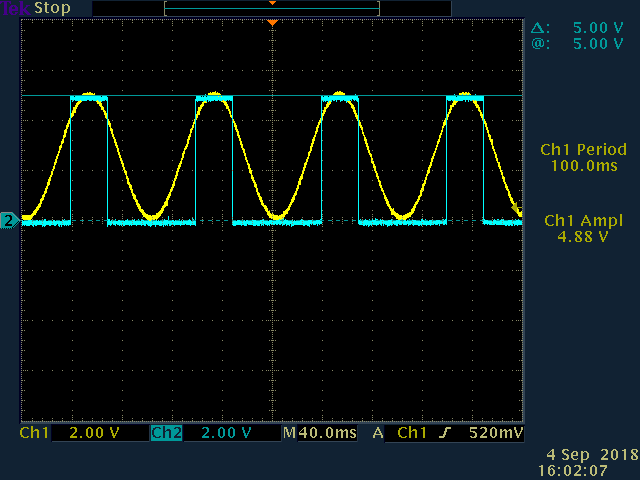
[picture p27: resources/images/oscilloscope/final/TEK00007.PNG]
Oscilloscope_sine_100_threshold_80


The period of the sine wave can be as high as 1 second. The image below shows this wave being generated fairly accurately, only 1.1% above the target period. Periods higher than 1 second are disabled, as above this value, you should consider switching to continuous-wave mode.

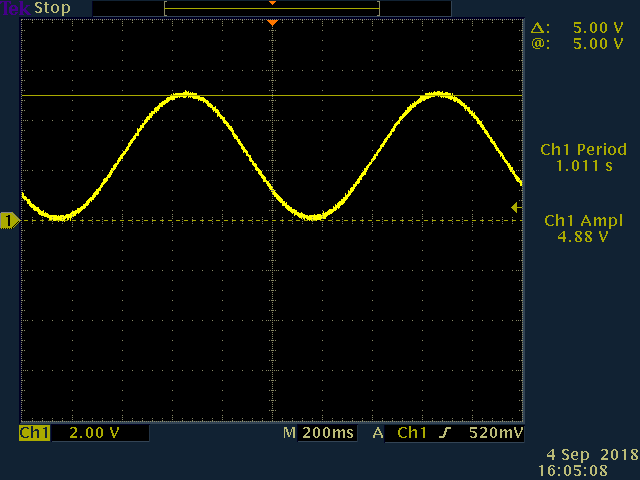
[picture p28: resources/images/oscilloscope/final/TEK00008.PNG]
Oscilloscope_sine_100_1s


The period of the sine wave can also pushed a lot lower than 100ms, but with some disadvantages. The image below shows a sine wave with a target period of 10ms, with a true value of 0.9% above the target. The wave is no longer smooth, and the time it takes for the DAC to update the voltage and the Arduino to calculate the next point on the wave becomes visible.

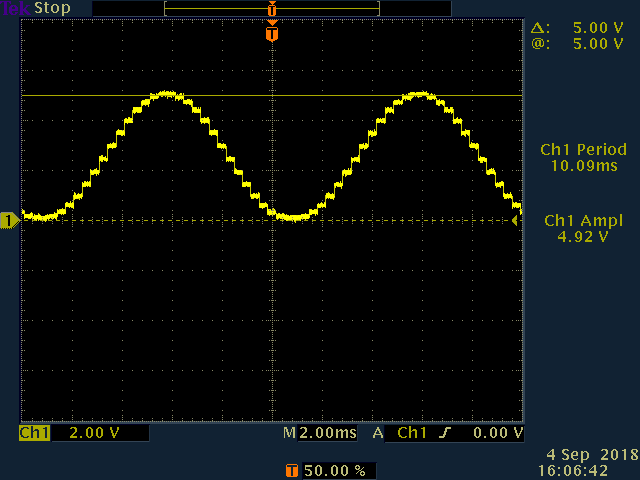
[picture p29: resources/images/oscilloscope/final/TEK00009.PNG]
Oscilloscope_sine_100_10ms


When this period is pushed even lower, the generated wave looks less like a sine wave and instead resembles a triangle wave. The target period of this wave is 2ms, but it is being generated with a period 16.7% higher than the target - a value no longer considered acceptably accurate.

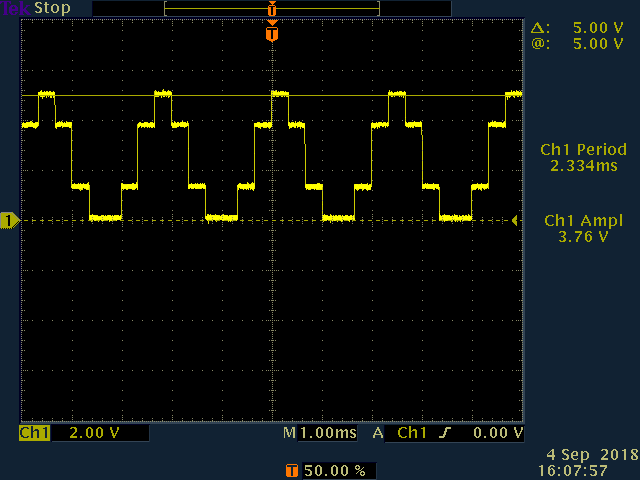
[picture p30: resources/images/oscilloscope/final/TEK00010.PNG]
Oscilloscope_sine_100_10ms


At the smallest possible period, the wave is no longer a sine wave. The square wave generated below is a sine wave with a target period of 1ms. The actual period is also 32.7% larger than the target. Due to this increase in inaccuracies with decreasing period targets, periods under 10ms are considered "inaccurate", and should only be used if higher frequencies are necessary (but using `square` as your modulation mode would give even higher frequencies with much higher accuracy).

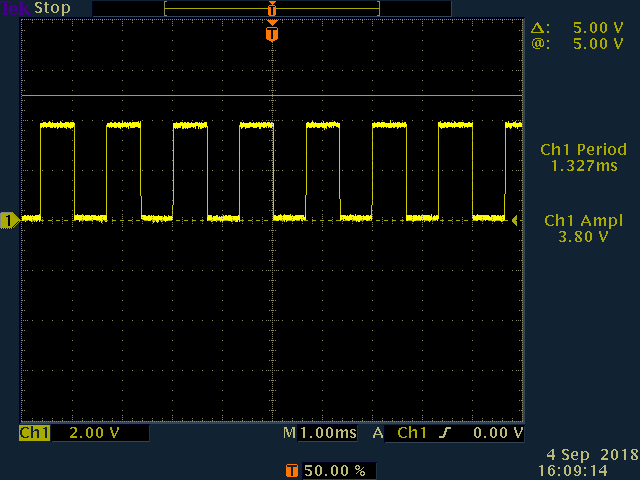
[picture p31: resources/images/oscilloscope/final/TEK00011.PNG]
Oscilloscope_sine_100_1ms


The same behaviour can be seen across other waveforms as well. The images below are for the `triangle` and `sawtooth` modulation modes.

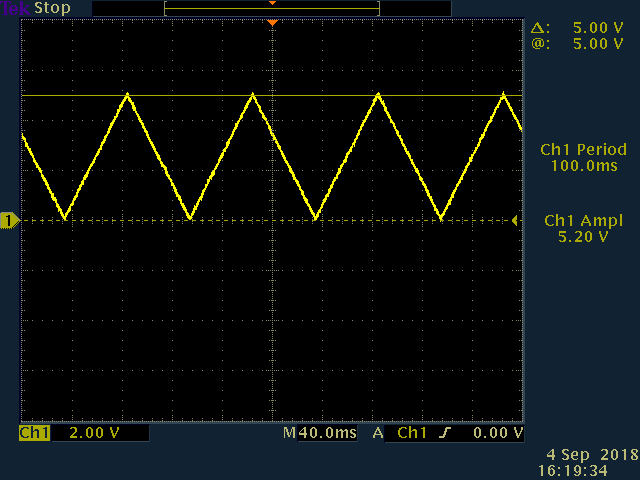
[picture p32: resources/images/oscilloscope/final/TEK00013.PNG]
Oscilloscope_triangle_100_100ms
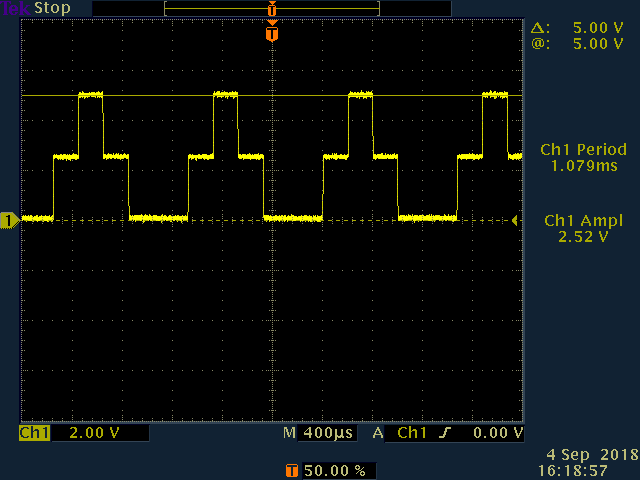
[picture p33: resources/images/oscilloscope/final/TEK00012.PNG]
Oscilloscope_triangle_100_1ms
|  |  |
|:-:|:-:|
| Triangle wave at 100ms target (exact) | Triangle wave at 1ms target (+7.9%) |

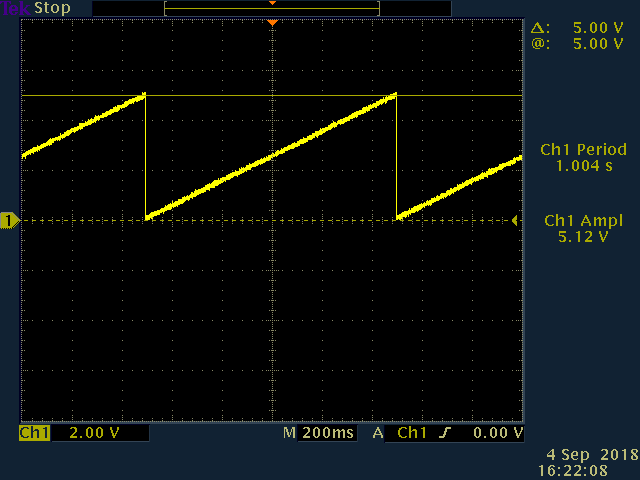
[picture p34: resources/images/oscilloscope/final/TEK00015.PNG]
Oscilloscope_sawtooth_100_1000ms
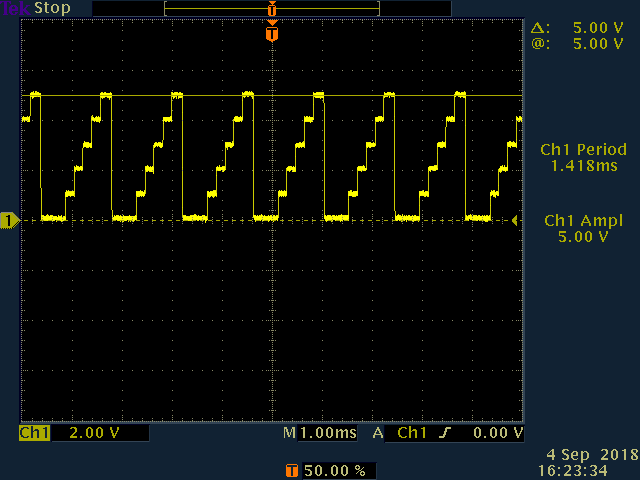
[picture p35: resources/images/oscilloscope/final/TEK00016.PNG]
Oscilloscope_sawtooth_100_1ms
|  |  |
|:-:|:-:|
| Sawtooth wave at (1s) 1000ms target (+0.4%) | Sawtooth wave at 1ms target (+41.2%) |

The final modulation mode available is `pulse`. A single pulse is defined by three parameters: the amplitude of the pulse, the length of the pulse, and the delay until the start of the successive pulse. This mode allows for pulses of length up to 1 hour, and as little as a millisecond. The following image shows a 100 millisecond pulse followed by a second pause, resulting in a perfect 1.1 second period.

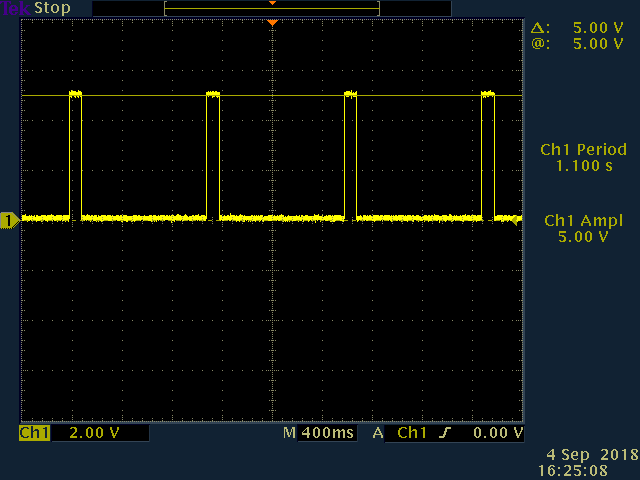
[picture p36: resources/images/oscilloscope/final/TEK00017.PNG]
Oscilloscope_sawtooth_100_1000ms


The following data gives the exact limits applied to the selection of the period for various modulation modes, and their measured corresponding deviations from the expected value:

| Modulation Mode | Period Limits | Needs calibration | Calibration Length | Typical [maximum] deviation (10ms - 100ms) | Typical [maximum] deviation (< 10ms) |
|:---------------:|:-------------:|:-----------------:|:------------------:|:------------------------------------------:|:------------------------------------:|
|      `none`     |      none     |         No        |         N/A        |                     N/A                    |                  N/A                 |
|      `sine`     |    1ms - 1s   |        Yes        |      5s - 10s      |                  +1% [+2%]                 |              +20% [+50%]             |
|     `square`    |   1ms - 1hr   |         No        |         N/A        |                 +0.5% [+1%]                |              +5% [+10%]              |
|    `triangle`   |    1ms - 1s   |        Yes        |      5s - 10s      |                  +1% [+2%]                 |              +20% [+50%]             |
|    `sawtooth`   |    1ms - 1s   |        Yes        |      5s - 10s      |                  +1% [+2%]                 |              +20% [+50%]             |
|     `pulse`     |   1ms - 1hr   |         No        |         N/A        |                 +0.5% [+1%]                |              +5% [+10%]              |

### Camera

The camera used in this project is the [Allied Vision Manta](https://www.alliedvision.com/fileadmin/content/documents/products/cameras/Manta/techman/Manta_TechMan.pdf
). It uses the Hirose HR10-10R-12PA(73) connector, for which we used the Hirose HR10A-10P-12S breakout cable. The pin numbering for the Hirose cable can be seen below:

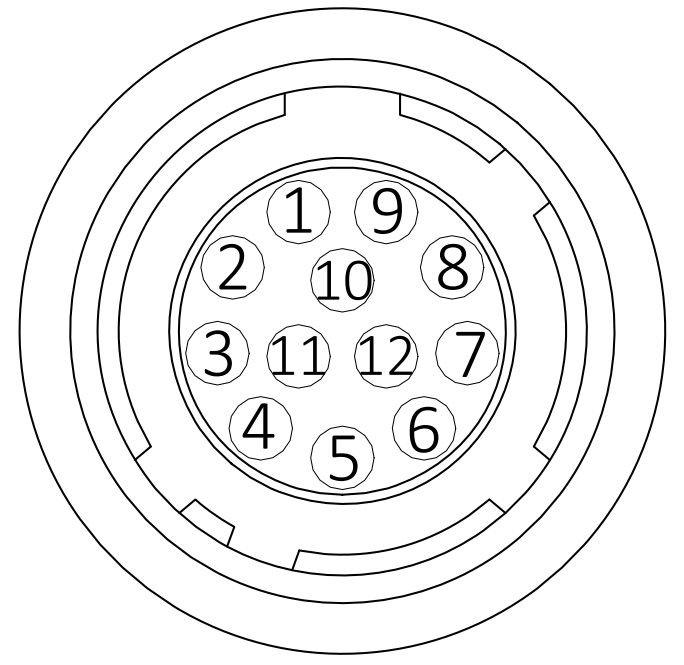
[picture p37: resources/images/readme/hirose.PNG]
Hirose


According to the input block diagram below (as well as Figure 109 in the documentation), both pins `In1` and `In2` are available as general purpose input pins, when connected to some isolated ground.

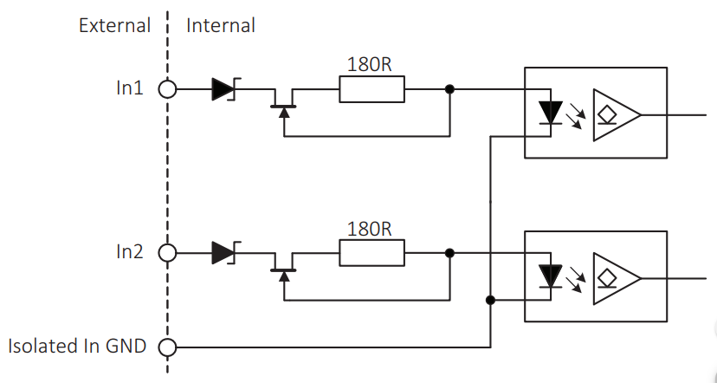
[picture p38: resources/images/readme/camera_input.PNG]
Camera Input


Similarly, the output block diagram below (as well as Figure 111 in the documentation) shows that pins `Out1` and `Out2` are available to use as general purpose output pins when the block is connected to some isolated power source, and the pins are pulled LOW using pull-down resistors. If the isolated power input is 5V, then both GPO pins will also signal at 5V.

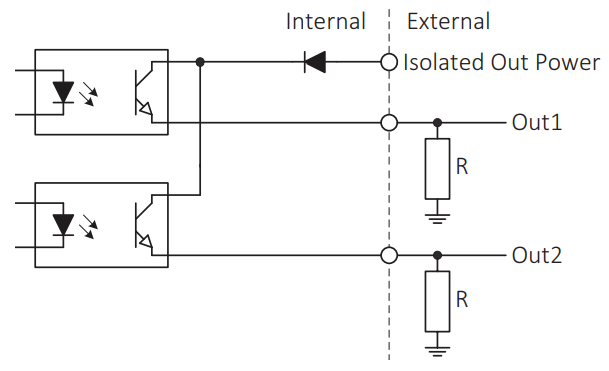
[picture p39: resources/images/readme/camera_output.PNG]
Camera Output


With this knowledge, it is possible to create a pin assignment table:

| Pin Number | Signal           | Assignment                                                                                                                          |
|------------|------------------|--------------------------------------------------------------------------------------------------------------------------------------|
| 4          | `In1`            | This pin can receive signal from the Arduino, and will synchronise the shutter of the camera with respect to the modulation waveform |
| 6          | `Out1`           | This pin will receive signal when a generated waveform amplitude reaches a threshold, triggering the shutter of the camera           |
| 7          | Isolated In GND  | This pin is tied to Arduino's GND pin                                                                                                |
| 10         | Isolated Out PWR | This pin is tied to Arduino's 5V pin                                                                                                 |

## The Software

### Server

CRATE A FILE FROM THIS AND HOST IT, AND CLEAN IT UP, LIKE ABOVE

[Unit]
Description=Python3 server
After = multi-user.target network.target network-online.target
Wants = network-online.target

[Service]
Type=idle
Restart=always
ExecStart=/usr/bin/python3 /home/pi/server.py

[Install]
WantedBy=multi-user.target

/lib/systemd/system/server.service

#### Client

### Parser

#### Table of Recognised Commands

### Error handler

#### Table of Errors and Warnings

(change to table of return codes?) (change warnings to stackable! 01+02+04 (up to 16?))

| Return Code | Return Code type |                         Description                          | More details given? |
| :---------: | :--------------: | :----------------------------------------------------------: | :-----------------: |
|     00      |     SUCCESS      |   The requested action completed without error or warning    |         No          |
|     01      |     WARNING      | The requested action was not carried out as it would have no effect |         No          |
|             |                  |                                                              |                     |

### Laser Serial Communication Script

### Arduino Controller Script (Python)

nohup

https://raspberrypi.stackexchange.com/questions/9695/disable-dtr-on-ttyusb0/31298#31298

https://linux.die.net/man/1/stty

#### Arduino Controller Script (C for AVR)

At the core of the Arduino Uno lies the Atmel ATmega328p microcontroller.

<MODES OF OPERATION, MODES OF MODULATION>

talk about why I had to replace the Wire library

http://dsscircuits.com/articles/arduino-i2c-master-library

changed compilation parameter to -O2 (talk about it) File --> Preferences --> Follow link at the bottom of page (using arduino 1.8.5)
"%USERPROFILE%\AppData\Local" on Windows, C:\Users\lyv26778\AppData\Local\Arduino15\preferences.txt, change all occurences (3) of -Os to -O2, restart Arduino IDE

## Licensing

## Author

Talk about me quickly, mention contact details, give supervisor details as well

## Acknowledgements

Same as pptx, + Hristo and Jess

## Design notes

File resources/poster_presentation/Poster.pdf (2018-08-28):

# Enhancing the functionality and adding remote control capability to an I14 instrument using a Raspberry Pi

Alexander Liptak, Diamond Light Source, Harwell Science and Innovation Campus, Didcot, Oxon OX11 0DE

The I14 beamline uses a laser for experiments that require sample illumination. In order to operate the laser, somebody would need to physically be in the same room as the laser and manually turn it on or off as required. This simple design had many drawbacks: mainly, remote operation of the laser was not possible, and one would need to break the safety interlock at I14 in order to control it.

Overcoming this inconvenience was the first motivation for this project, an so the development of a smart networked laser controlled by a Raspberry Pi began. On top of this requirement, it soon became clear that a smart laser can do more than just switch on and off remotely. Consequently, the specification of this project was updated to include the ability to modulate the output of the laser using custom waveforms that could be generated on-demand, as well as other features like synchronizing a camera on the instrument with the laser.

The Raspberry Pi (RPi) is a single-board computer about the size of a credit card, chosen to act a server in
this project due to its small size, lots of low-level peripherals, and performance comparable to a
low-cost general-purpose PC.

The RPi runs a Python-based “server”, or a series of Python scripts that allow the RPi to securely
communicate over the Local Area Network
(LAN) with other networked devices, as well as
communicate directly with the attached laser and Arduino (discussed later). The server is composed of 5 distinct Python scripts, the combination of which allows the RPi to receive commands from any device on the LAN, carry out some action on the laser in a safe way, and return an appropriate response.

The first part is the “main server”, a script in charge of
listening for incoming connections, accepting a single
connection at any one time, and formatting a response in a way that the “client” (or user) expects to receive it in.
The second is the “parser”, a script in charge of understanding what the received commands mean, executing appropriate actions, and rejecting commands that are not recognized or contain wrong parameters.
The third part is the “laser controller”, which is responsible
for communicating with the laser over a serial interface, and carrying out tasks such as turning the laser on and off, tweaking its settings and checking its status for any errors.
The fourth is the “Arduino controller” (described further in
section III), which communicates with the Arduino over the
serial and GPIO interfaces, in order to generate waveforms that will modulate the output of the laser. The final, and arguably most important script, is the error handler: it checks if the laser, Arduino or the server itself perform the requested actions as expected, and returns a useful message to the user instead of letting the server crash.
I. Introduction | II. Raspberry Pi: Server

The Arduino is a single-board microcontroller: a device that can execute some code, much like a computer, designed for use in embedded systems. Unlike the RPi, which runs a Linux-based operating system in addition to the Python server, the Arduino will exclusively execute only the code that it is flashed with. This means that an Arduino will, in most cases, execute code many times faster than the RPi.

“Real-time” execution of code makes the Arduino well suited for generating high-resolution signals that will be used to
modulate the laser. The Arduino communicates with the
RPi over a serial interface in order to obtain the values for frequency, amplitude, and duty cycle of the wave to be generated. It also communicates with the RPi using
its GPIO interface, where a combination of digital
pin values corresponds to a shape of the wave that
the Arduino will generate. Finally, the Arduino sends
the generated wave data as a 12-bit number to a DAC over the I

2C interface (discussed further in section IV).

Pulse Width Modulation (PWM) is a technique for
mimicking analog signal by a rapidly alternating digital signal (a square wave). Arduino’s support for hardware PWM is the reason why all LED and buzzer signaling in this projects is carried out on the Arduino.

Raspberry Pi is a trademark of the Raspberry Pi Foundation

# III. Arduino: Controller

A digital-to-analog converter (DAC) is a type of device that converts a digital signal into an analog signal. The MCP4725 is one of these devices,
converting a 12-bit binary number into a variable voltage, which is
used as a signal to modulate the laser. The DAC is updated
hundreds of times per second with values that correspond to different points on a wave. The Arduino carries out a “calibration phase” on the DAC with every waveform to ensure its frequency is accurate. The calibrated wave will usually compensate for the time
it takes to update the DAC by skipping a number of points on
the wave.

As a safety feature, the DAC power supply is connected directly to the safety interlock of the beamline. Opening the door instantly cuts off the power to the DAC, modulating the laser amplitude to zero.

# IV. DAC: Modulation

This project originated from a noticeable room for improvement of one of the components on the I14 beamline, but as it was nearing its completion, it became clear that it also opened up more room for improvement on other components across other beamlines.

The foundation for a smart networked controller that would, with little
need for additional programming, enable the remote control, monitoring
and automation of a component it is attached to, is something I believe many other would find useful. The outcome of this project will hopefully
inspire, and possibly even guide other beamline scientists when
networking their own components.

The server in this project uses a custom network protocol that conforms to Diamond’s serial protocol guidelines. The error handler allows for easy implementation of custom errors and warnings, and the parser can be edited relatively easily to define custom commands and parameters, and associate them with some corresponding functionality.

# V. Conclusion

Thank you to Fernando Cacho-Nerin and Edmund Warwick for supervising me and guiding me through this project. A thank you also goes Ben Garvey for all his help with the various electronics issues and requests I had. A further thanks goes to the Diamond IT team (Richard Cooper in particular) for getting the RPi on the network. Finally, a special thanks to the Diamond Students team, without which this project would not be possible.

# Acknowledgements

For more information please visit www.diamond.ac.uk
Alternatively, contact Fernando Cacho-Nerin at fernando.cacho-nerin@diamond.ac.uk or Edmund Warrick at edmund.warrick@diamond.ac.uk

Credit to Element 14
Link: http://au.element14.com/buy-raspberry-pi

"A Arduino Uno board" by JotaCartas, obtained from Wikimedia Commons, is licensed under CC BY 2.0

Arduino is a trademark of Arduino AG

Credit to Adafruit
Link: https://www.adafruit.com/product/935

Generated with www.qrcode-monkey.com

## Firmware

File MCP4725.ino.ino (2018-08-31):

/******************************************************************************
 **                                                                          **
 **     Written by Alexander Liptak (GitHub: @ajulik1997)                    **
 **     Date: Summer 2018                                                    **
 **     E-Mail: Alexander.Liptak.2015@live.rhul.ac.uk                        **
 **     Phone: +44 7901 595107                                               **
 **                                                                          **
 ******************************************************************************/

/******************* MCP4725 DAC Controller for Arduino Uno *******************/

/***** MODES OF MODULATION ***** P[4,7,8] *****
    000: none [DEFAULT]
    001: sine
    010: square
    011: triangle
    100: sawtooth
    111: pulse
 **********************************************

 ***** MODES OF OPERATION ***** P[A0,A1] ******
   00: undefined
   01: master
   10: gated (NOTE: only works with mode 010)
   11: independent [DEFAULT]
 **********************************************/

#include "I2C.h"    // instead of Wire library, as it times out instead of locks up when transmission fails
#include "math.h"   // for computing sine, rounding, etc.

/************************ Global variable declarations ************************/

// MODULATION VARIABLES
uint16_t power = 0;      // Power of laser: 0-4095
uint32_t tot_micro = 0;  // MICROseconds that a full cycle should last (period)
uint32_t off_micro = 0;  // MICROseconds delay between cycles

// WAVE VARIABLES
bool needs_calibrating = true;  // Wave needs calibrating
bool waiting = true;            // Is wave waiting until delay is complete?
float divisor = 1.0;            // How many steps per wave (more steps, nicer wave, lower frequency)
float increment = 0.01;         // How much to increment the divisor (prevents calibration from taking too long)
unsigned long timer = 0;        // Wave timer (how long did my wave take, compared to target time)
unsigned long last_timer = 0;   // Wave timer, so we can revert to this in case we overincrement during alibration
float threshold = 50.0;      // Threshold of power above which laser triggers camera

// STATE VARIABLES
bool interlock_open = true;     // State of gate
bool override_on = true;        // State of interlock
bool periodic_warning = true;   // State of warning light / buzzer (blinking)
bool constant_warning = true;   // State of warning light / buzzer (constant)
char rgb_state = ' ';           // State of LED
uint8_t modeOfModulation = 0;   // Mode of modulation (none/sine/square/triangle/sawtooth/pulse)
uint8_t modeOfOperation = 3;    // Mode of operation (gated/master/independent)

// WARNING BEEP VARIALBES
unsigned long warn_timer = 0;   // Warning timer (for measuring time between beeps)
uint32_t warn_delay = 5e5;      // Warning delay (time to wait between beeps)

/************************** Function predeclarations **************************/

// MODULATION FUNCTIONS
inline void none();
inline void sine();
inline void square();
inline void triangle();
inline void sawtooth();
inline void pulse();

// HELPER FUNCTIONS
void writeToDAC(uint16_t);
void setRGB(char);
inline void calibrate();
inline void trigger(uint16_t);
inline void genericOff();

// PERIODIC CHECK FUNCTIONS
void check();
inline void checkInterlock();
inline void checkForSerial();
inline void checkModulationMode();
inline void checkOperationMode();

/********* writeToDAC ****** writes data to DAC register (not EEPROM) *********/

void writeToDAC(uint16_t val) {
  uint8_t bytes[2] = {val / 16, (val % 16) << 4}; // 16-bit int -> 2x8-bit ints
  I2c.write(0x62, 0x40, bytes, 2);    //0x62 - DAC Address, 0x40 - DAC Register
}

/******** setRGB ****** set RGB LED to colour represented by parameter ********/

void setRGB(char colour) {
  // override some colours on warnings
  if (colour == 'K' || colour == 'B' || colour == 'M') {
    if (periodic_warning) {
      colour = 'O';
    } else if (constant_warning) {
      colour = 'R';
    }
  }

  // if the same colour is already set, return from function, else set colour
  if (rgb_state == colour) return;
  rgb_state = colour;

  // set LED colour as requested
  switch (colour) {

    // ALWAYS ACCESSIBLE COLOURS
    case 'R': analogWrite(9, 64); analogWrite(10, 0); analogWrite(11, 0);  break; //RED     : INTERLOCK
    case 'G': analogWrite(9, 0); analogWrite(10, 0); analogWrite(11, 64);  break; //GREEN   : SERIAL
    case 'O': analogWrite(9, 64); analogWrite(10, 0); analogWrite(11, 8);  break; //ORANGE  : OVERRIDE

    // ACCESSIBLE WHEN NO WARNING
    case 'K': analogWrite(9, 0); analogWrite(10, 0); analogWrite(11, 0);   break; //KEY     : OFF
    case 'B': analogWrite(9, 0); analogWrite(10, 64); analogWrite(11, 0);  break; //BLUE    : LASER
    case 'M': analogWrite(9, 64); analogWrite(10, 64); analogWrite(11, 0); break; //MAGENTA : CALIB

      // DISABLED COLOURS
      //case 'W': analogWrite(9, 64); analogWrite(10, 64); analogWrite(11, 64); break;  //WHITE
      //case 'Y': analogWrite(9, 64); analogWrite(10, 0); analogWrite(11, 64); break;   //YELLOW
      //case 'C': analogWrite(9, 0); analogWrite(10, 64); analogWrite(11, 64); break;   //CYAN
  }
}

/*** calibrate ** adjusts steps per period of wave for requested frequency  ***/
// STILL NEED TO HAVE A LOOK AT THIS (percentage, fallback, idk idk, takes too long with low power? + comment on it!!) !!!!!!!!
inline void calibrate() {
  // to avoid micros from increasing while executing function
  unsigned long temp_timer = micros();
  
  // is the wave long enough
  if ((micros() - timer) <= (tot_micro)) {
    divisor = divisor + increment;
    return;
  }

  // did we overstep? which is closer?
  if ((fabs(temp_timer - timer) - tot_micro) > (fabs(temp_timer - last_timer) - tot_micro)){
    divisor = divisor - increment;
    return;
  }

  // finished calibrating
  needs_calibrating = !needs_calibrating;
  
}

/** trigger * if mode of operation is "master", signal pin in sync with wave **/

inline void trigger(uint16_t val) {
  if (val > threshold*power) {
    digitalWrite(3, HIGH);
    return;
  }
  digitalWrite(3, LOW);
}

/** genericOff *** generic function that switches off the DAC once if needed **/

inline void genericOff() {
  if (needs_calibrating) {       // resued bool to ensure this only happens once
    writeToDAC(0);               // switch DAC off
    needs_calibrating = false;
  }
  setRGB('K');                   // signal off, no longer lasing
}

/****** check ***** wrapper function for all checks that need to be done ******/

void check() {
  checkInterlock();
  checkForSerial();
  checkModulationMode();
  checkOperationMode();
}

/****** checkInterlock ***** checks the status of interlock and override ******/

inline void checkInterlock() {
  // pin status to useful variables
  interlock_open = not digitalRead(A3);
  override_on =  digitalRead(A2);

  // safety interlock is open, we need to find out if it is safe to continue
  if (interlock_open) {

    // override is on, we can continue but flash an orange warning light (and buzzer)
    if (override_on) {

      // if we came here from inerlock open and override not on, clear that
      constant_warning = false;
      // if time between waiting has elapsed toggle states
      if (micros() - warn_timer > warn_delay) {
        warn_timer = micros();
        periodic_warning = !periodic_warning;
        // LED orange and buzzer on for half a second
        if (periodic_warning) {
          analogWrite(6, 64);
          warn_delay = 5e5;
          setRGB('O');
          // LED black and buzzer off for 5 seconds
        } else {
          analogWrite(6, 0);
          warn_delay = 5e6;
          setRGB('K');
        }
      }
      return;
    } else {
      // interlock is open and override is not on, cut power and signal red (do this only once)
      if (!constant_warning) {
        constant_warning = true;
        periodic_warning = false;
        power = 0;
        analogWrite(6, 64);
        setRGB('R');
      }
      return;
    }
  } else {
    // interlock is closed, we don't care about override, switch off all warnings (only once)
    if (constant_warning || periodic_warning) {
      constant_warning = false;
      periodic_warning = false;
      analogWrite(6, 0);
      setRGB('K');
    }
    return;
  }
}

/***** checkForSerial ***** checks for incoming serial data and parses it *****/

inline void checkForSerial() {
  // only do anything if data is waiting to be parsed
  if (Serial.available() > 0) {
    setRGB('G');                                    // we are busy with serial communication
    String str = Serial.readString();               // get one line from Serial
    uint8_t str_index = 0;                          // start from first character
    while (str_index != str.indexOf("\r\n")) {      // if we have not reached the end
      while (str.indexOf(" ", str_index) != -1) {   // if we have not reached the last space
        float val = str.substring(str_index + 1, str.indexOf(" ", str_index)).toFloat();  // extract float
        switch (str.charAt(str_index)) {            // first character signals what float means, sort accordingly
          case 'A': power = round(4095 * (val / 100.0)); break;
          case 'T': threshold = val / 100.0; break;
          case 'P': tot_micro = round(val * 1e3); increment = pow(tot_micro, 2) / (5e9) + 0.001; break;
          case 'D': off_micro = round(val * 1e3); break;
        }
        str_index = str.indexOf(" ", str_index) + 1; // continue to next space
      }
    }
    Serial.println("OK");       // signal transmission successful
    needs_calibrating = true;   // set calibration flag
    divisor = 1.0;              // reset wave divisor
    setRGB('K');                // LED off, transmission complete
  }
}

/***** checkModulationMode ****** detects the mode of modulation of laser *****/

inline void checkModulationMode() {
  // gets mode of modulation as a number from combination of three pins
  modeOfModulation = 4 * (uint8_t)(digitalRead(4)) +
                     2 * (uint8_t)(digitalRead(7)) +
                     1 * (uint8_t)(digitalRead(8));
}

/****** checkOperationMode ****** detects the mode of operation of laser ******/

inline void checkOperationMode() {
  // gets mode of operation as a number from combination of two pins
  modeOfOperation = 2 * (uint8_t)(digitalRead(A0)) +
                    1 * (uint8_t)(digitalRead(A1));
}

/*************************** MODE 000: No modulation **************************/

inline void none() {
  delayMicroseconds(16);    // necessary for Pi to settle pins before reading
  needs_calibrating = true; // not really calibration, but reusing variable

  // should stay in this loop until modulation mode is changed
  while (modeOfModulation == 0) {
    check();

    // only change the DAC value if it needs to be changed
    if (needs_calibrating) {
      writeToDAC(power);
      needs_calibrating = false;
    }

    // if power is off, set LED to black
    if (power == 0) {
      setRGB('K');
      continue;
    }

    // set LED to blue, we a lasing
    setRGB('B');
  }
}

/*********************** MODE 001: Sine wave modulation ***********************/
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

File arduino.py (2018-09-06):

###############################################################################
###                                                                         ###
###     Written by Alexander Liptak (GitHub: @ajulik1997)                   ###
###     Date: Summer 2018                                                   ###
###     E-Mail: Alexander.Liptak.2015@live.rhul.ac.uk                       ###
###     Phone: +44 7901 595107                                              ###
###                                                                         ###
###############################################################################

import RPi.GPIO as GPIO
import subprocess
import serial
import time

## SET UP GPIOs ###############################################################

GPIO.setmode(GPIO.BCM)
GPIO.setwarnings(False)
GPIO.setup(25, GPIO.OUT)                ## Arduino reset pin
GPIO.setup([22, 27, 17], GPIO.OUT)      ## Modulation mode switch signals
GPIO.setup([16, 26], GPIO.OUT)          ## Operation mode switch signals

## RESET ARDUINO ##############################################################

def reset():
    '''RESETS ARDUINO TO KNOWN STATE AND PREPARES FOR COMMUNICATION'''

    try:
        subprocess.run("stty -F /dev/ttyACM0 -hupcl", shell=True, check=True)
    except subprocess.CalledProcessError as e:
        return (['35', str(e)])

    GPIO.output([22, 27, 17], GPIO.LOW)
    GPIO.output([16, 26], GPIO.LOW)

    GPIO.output(25, GPIO.HIGH)
    time.sleep(0.1)
    GPIO.output(25, GPIO.LOW)

## PRIVATE FUNCTIONS ##########################################################

def sendSerial(string, path='/dev/ttyACM0'):
    try:
        with serial.Serial(port = path,
                           baudrate = 9600,
                           timeout = 5,
                           dsrdtr = False) as ser:
            ser.write((string + ' \r\n').encode(encoding='ascii'))
            time.sleep(0.1)
            response = ser.readline()
            if response == b'OK\r\n':
                return('00')
            elif response == b'':
                return('32')
            else: return(['34', str(response)])
    except serial.SerialException as e:
        return(['31', str(e)])
    except Exception as e:
        return(['30', str(e)])

## PUBLIC FUNCTIONS ###########################################################

def setLaserPower(pwr):
    '''
    Sets power of laser via Serial port

    Arguments:
        pwr <float> [0.0 - 100.0] - laser power as a percentage

    Returns:
        Error codes (see local file errors.txt)
    '''

    return(sendSerial("A" + str(pwr)))


def setOperationMode(mode):
    '''
    Sets the operation mode of laser via GPIO

    Arguments:
        mode <str> - string describing operation mode of laser
            gated:  laser is triggered via camera GPIO
            master: camera is triggered via laser GPIO
            indep:  laser and camera operate independently

    Returns:
        none
    '''

    if mode == 'gated':  GPIO.output([16, 26], (GPIO.HIGH, GPIO.LOW))
    if mode == 'master': GPIO.output([16, 26], (GPIO.LOW,  GPIO.HIGH))
    if mode == 'indep':  GPIO.output([16, 26], (GPIO.HIGH, GPIO.HIGH))

    
def setTriggerThreshold(pwr):
    '''
    Sets the percentage of power above which laser can trigger camera in "master" mode

    Arguments:
        pwr <float> [0.0 - 100.0] - laser power as a percentage

    Returns:
        Error codes (see local file errors.txt)
    '''

    return(sendSerial("T" + str(pwr)))
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

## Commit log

2018-07-20 Added LASER_MAINS
2018-07-20 Created folder for flowcharts
2018-07-20 Added LASER_MAINS.xml
2018-08-30 Finalised Arduino script
2018-08-31 Final Arduino laser controller
2018-09-03 Updated Schematic
    [full_schematic.fzz]
2018-09-04 Updated Raspberry Pi routing
    [full_schematic.fzz]
2018-09-05 Updated pin assignements
2018-09-06 Updated pin configuration
2018-09-06 Updated pin numbering
2018-09-25 Updated documentation with wiring images
